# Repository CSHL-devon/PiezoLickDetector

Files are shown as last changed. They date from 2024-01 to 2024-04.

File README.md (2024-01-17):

# Piezo Lick Detector

An amplifier for detecting rodent licks using piezo-based sensor systems

## General Use

Each board has three channels that can receive separate input from three different piezo sensors. Each channel has independently controllable gain and dual outputs: raw analog voltage and 5V TTL.

### Piezo Concerns

- We use 12mm piezo disks that are extremely common and cheap. 

- "Positive" input on the amp is considered the crystal side of the piezo (the white center of the disk/strip) and "negative" the surrounding copper. If you wire it backwards, you will still get a signal (piezo output is AC), but it may not be the side of the signal you want. The amp cuts anything below zero as it enters the circuit, so depending on the orientation of the piezo in the sensor, or with respect to the animal, the "positive" voltage swing may be bigger, or smaller than the "negative" swing when the animal licks. Best practice is just to test output response once the system is in place and wire it the way you get the biggest signal.

- If you're solding the wires to the piezo yourself, take care not to overheat the piezo. Even if it doesn't visibly delaminate the piezo, you could do enough unseen damage to end up with a poor sensor. If you're not confident in your soldering skills, piezos are available pre-wired.

- This is a voltage-mode piezo amp. The length of the wire between the piezo and the amp should be kept to a minimum, else the capacitance of the cable will start to interfere with the sensor.

### Gain

The gain of the amplifier is adjusted using the round trimmer marked "Gain" for the appropriate channel. This trimmer is multi-turn to add some precision to the adjustments, however it has no stops to indicate the start, or end of the range. On first use, it's a good idea to simply turn it counter-clockwise several (~10) full turns to be sure you're at the bottom and then slowly work your way up until you reach the desired signal.  

Choosing the correct gain can be tricky with piezo-based systems and the quality of the detection you get will depend on the type of piezo/lick-spout you deploy, the placement of your sensor with respect to the animal and how well the sensor is physically isolated from other sources of shock/vibration. This is not trivial and takes some practice to get your setup and positioning perfect. 

### Threshold

The 5V TTL output is based on thresholding the raw voltage signal. That threshold is controlled using the square single-turn trimmer labeled "Threshold" for the appropriate channel. The available threshold does not cover the entire 0-5V range of the device. By default, it covers 2.5V-3.75V. This range was found (for our purposes) to encompass the best gain settings for noise when the setup is well optimized. You can, of course alter the range by changing the values of R2, R9 and R10 (as an example for channel 1) if you find it doesn't suit your use-case, but the default is a good starting point. You could also just bring the raw signal in through a DAQ and threshold in software if that suits your setup design.

## Building

This project came before I started converting all my projects to through-hole, so most of the parts are surface-mount. It's not too bad and If you practice a bit with a rework station you can get through it. If you have access to a surface-mount oven it's easy. Otherwise, there are many services that will populate the board with the parts for you. 

I may eventually get around to updating this to through-hole construction, but you can also just build it on a breadboard, or an Adafruit perma-proto board by following the schematic, without the custom PCB. This is probably the easiest way to get up and running for the least money and all of the parts I've used have through-hole equivalents.

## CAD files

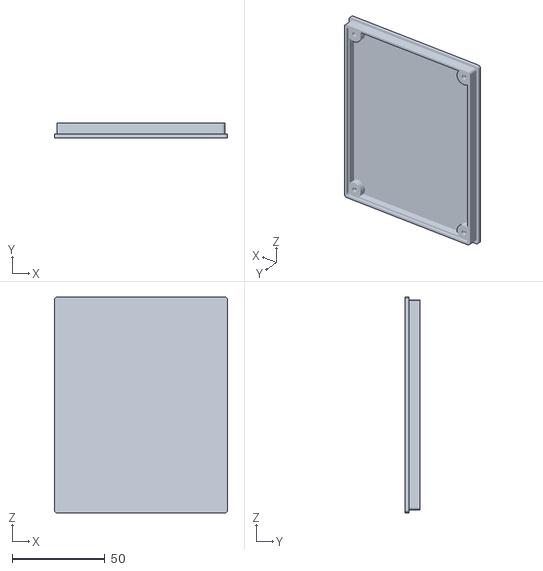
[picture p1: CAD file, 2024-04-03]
CAD/3DPrint/BoardMount.stl
93.5 x 8.00 x 116.5

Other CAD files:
CAD/3DPrint/BoardMount.ipt

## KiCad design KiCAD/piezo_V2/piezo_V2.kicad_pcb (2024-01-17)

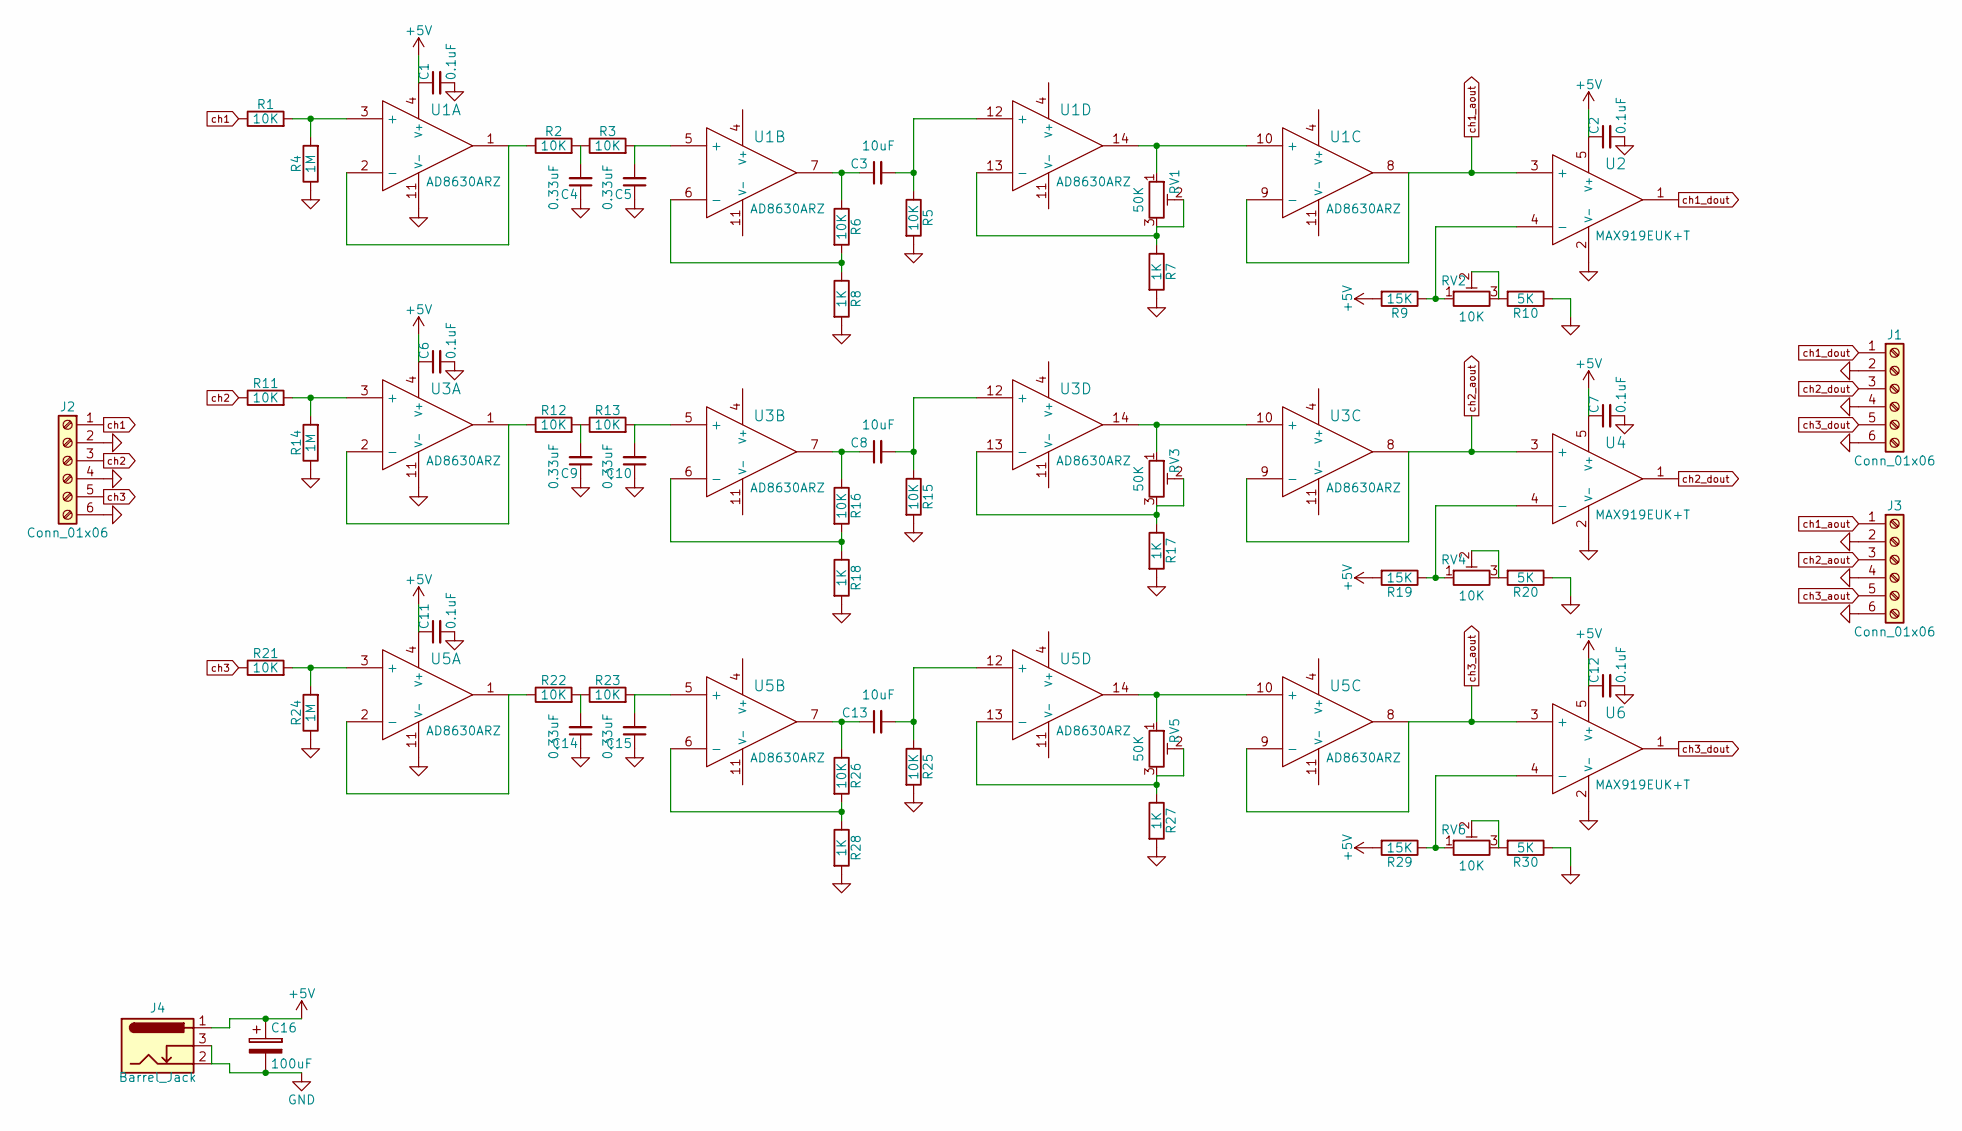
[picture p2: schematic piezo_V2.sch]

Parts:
C1, C2, C6, C7, C11, C12: 0.1uF; C_1206_HandSoldering
C3, C8, C13: 10uF; C_1206_HandSoldering
C4, C5, C9, C10, C14, C15: 0.33uF; C_1206_HandSoldering
C16: 100uF; CP_Radial_D8.0mm_P3.50mm
J1, J2, J3: Conn_01x06; EM280206_6P_Terminal
J4: Barrel_Jack; PJ-079AH-DCJACK
R1, R2, R3, R5, R6, R11, R12, R13, R15, R16, R21, R22, R23, R25, R26: 10K; R_1206_HandSoldering
R4, R14, R24: 1M; R_1206_HandSoldering
R7, R8, R17, R18, R27, R28: 1K; R_1206_HandSoldering
R9, R19, R29: 15K; R_1206_HandSoldering
R10, R20, R30: 5K; R_1206_HandSoldering
RV1, RV3, RV5: 50K; 50K_Trimmer_Bourns_3339P
RV2, RV4, RV6: 10K; 10K_Trimmer_Bourns_3362P
U1, U3, U5: AD8630ARZ
U2, U4, U6: MAX919EUK+T; TMAX9140EUK+T

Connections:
+5V: C1.1, C2.1, C6.1, C7.1, C11.1, C12.1, C16.1, J4.1, R9.2, R19.2, R29.2, U1.4 (V+), U2.5 (V+), U3.4 (V+), U4.5 (V+), U5.4 (V+), U6.5 (V+)
GND: C1.2, C2.2, C4.1, C5.1, C6.2, C7.2, C9.1, C10.1, C11.2, C12.2, C14.1, C15.1, C16.2, J1.2, J1.4, J1.6, J2.2, J2.4, J2.6, J3.2, J3.4, J3.6, J4.2, J4.3, R4.1, R5.2, R7.2, R8.2, R10.1, R14.1, R15.2, R17.2, R18.2, R20.1, R24.1, R25.2, R27.2, R28.2, R30.1, U1.11 (V-), U2.2 (V-), U3.11 (V-), U4.2 (V-), U5.11 (V-), U6.2 (V-)
unnamed: C3.1, R6.1, U1.7
unnamed: C3.2, R5.1, U1.12 (+)
unnamed: C4.2, R2.2, R3.1
unnamed: C5.2, R3.2, U1.5 (+)
unnamed: C8.1, R16.1, U3.7
unnamed: C8.2, R15.1, U3.12 (+)
unnamed: C9.2, R12.2, R13.1
unnamed: C10.2, R13.2, U3.5 (+)
unnamed: C13.1, R26.1, U5.7
unnamed: C13.2, R25.1, U5.12 (+)
unnamed: C14.2, R22.2, R23.1
unnamed: C15.2, R23.2, U5.5 (+)
unnamed: R1.2, R4.2, U1.3 (+)
unnamed: R2.1, U1.1, U1.2 (-)
unnamed: R6.2, R8.1, U1.6 (-)
unnamed: R7.1, RV1.2, RV1.3, U1.13 (-)
unnamed: R9.1, RV2.1, U2.4 (-)
unnamed: R10.2, RV2.2, RV2.3
unnamed: R11.2, R14.2, U3.3 (+)
unnamed: R12.1, U3.1, U3.2 (-)
unnamed: R16.2, R18.1, U3.6 (-)
unnamed: R17.1, RV3.2, RV3.3, U3.13 (-)
unnamed: R19.1, RV4.1, U4.4 (-)
unnamed: R20.2, RV4.2, RV4.3
unnamed: R21.2, R24.2, U5.3 (+)
unnamed: R22.1, U5.1, U5.2 (-)
unnamed: R26.2, R28.1, U5.6 (-)
unnamed: R27.1, RV5.2, RV5.3, U5.13 (-)
unnamed: R29.1, RV6.1, U6.4 (-)
unnamed: R30.2, RV6.2, RV6.3
unnamed: RV1.1, U1.10 (+), U1.14
unnamed: RV3.1, U3.10 (+), U3.14
unnamed: RV5.1, U5.10 (+), U5.14
ch1: J2.1, R1.1
ch1_aout: J3.1, U1.8, U1.9 (-), U2.3 (+)
ch1_dout: J1.1, U2.1
ch2: J2.3, R11.1
ch2_aout: J3.3, U3.8, U3.9 (-), U4.3 (+)
ch2_dout: J1.3, U4.1
ch3: J2.5, R21.1
ch3_aout: J3.5, U5.8, U5.9 (-), U6.3 (+)
ch3_dout: J1.5, U6.1

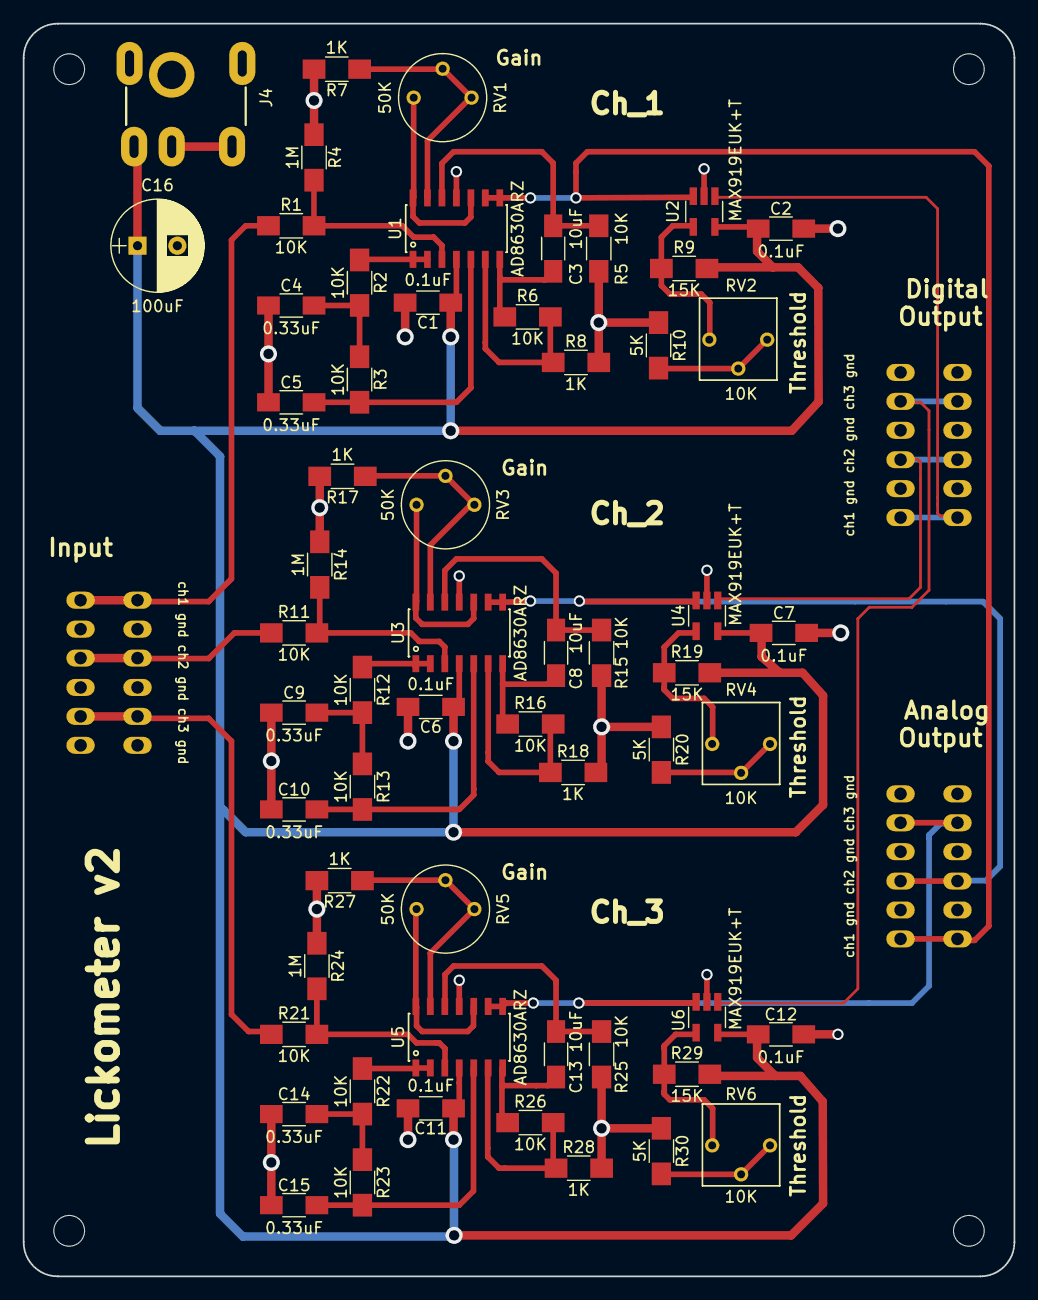
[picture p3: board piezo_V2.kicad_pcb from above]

Board: 2 copper layers, 87.0 x 110.0 mm, 62 parts (0 on the bottom side), 44 nets.

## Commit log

2024-01-17 Add README, Update Symbols on Schematic
    [piezo_V2.kicad_sch]
2024-04-03 Final CSHL
    [BoardMount.ipt, BoardMount.stl]
